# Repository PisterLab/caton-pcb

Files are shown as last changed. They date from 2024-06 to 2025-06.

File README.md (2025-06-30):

# Caton PCB: A Wireless EEG System for Concurrent TMS-EEG-fMRI

Caton is an open-source, wireless EEG system designed to address the challenges of concurrent TMS-EEG-fMRI studies. By eliminating long wires and large loop areas typical in traditional EEG systems, Caton aims to provide a safer and more effective platform for multimodal brain imaging and stimulation. This repository contains the hardware design files for the Caton project.

This work was published at ISMRM 2025.

## Overview

Concurrent TMS-EEG-fMRI measurements offer improved insights into human brain function, combining high temporal and spatial resolution with causal intervention. However, the long wires in traditional EEG systems pose substantial safety and signal integrity concerns in the MRI environment.

This project introduces a wireless EEG system based on the Single Chip Micro Mote (SCµM). The goal is to enable safer, more effective multimodal brain imaging studies by minimizing wire-induced artifacts and risks. We have developed and validated a prototype system that integrates the SCµM-3C with the Texas Instruments ADS1299 on an MRI-safe PCB. Our results show stable wireless operation from within the MRI bore with minimal disruption from MRI sequences.

## System Architecture

The Caton system is designed to be modular, allowing for flexible development and testing. The main components are the `Caton-M-TRAD` motherboard and compatible daughterboards like the `Caton-D-Q100`.

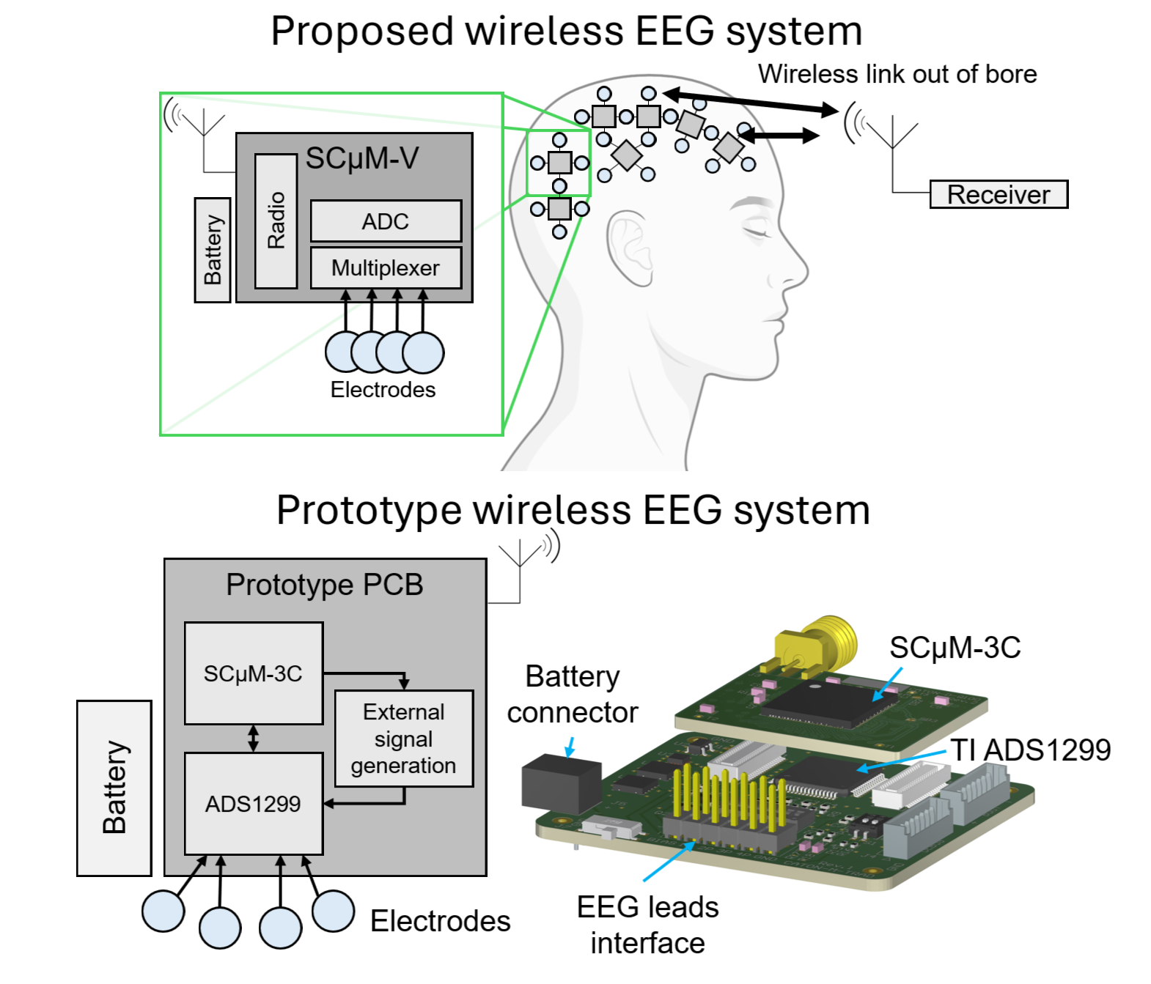
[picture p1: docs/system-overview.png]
System Overview


### Caton-M-TRAD (Motherboard)

`Caton-M-TRAD` is the main motherboard that houses the core circuitry for EEG signal acquisition and power management. It is a traditional PCB that includes:
- The Texas Instruments ADS1299 EEG analog front-end.
- Four power regulators for the different voltage domains:
    - 5V buck-boost for ADS1299 AVDD
    - 1.8V LDO for ADS1299 DVDD
    - 1.8V LDO for SCµM-3C VBAT/VDDIO
    - 1.1V LDO for SCµM-3C VDD
- 2x 20-pin mezzanine connectors for interfacing with daughterboards.
- GPIO jumpers.
- An electrode connector.

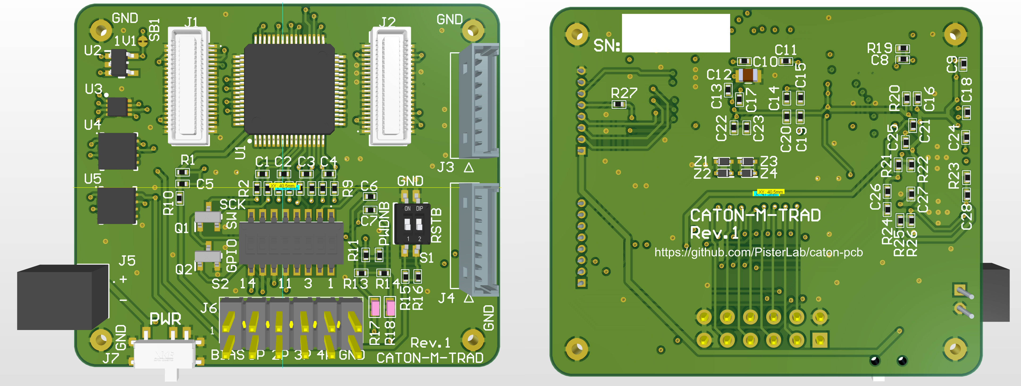
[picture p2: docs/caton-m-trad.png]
Caton-M-TRAD Diagram


### Caton-D-Q100 (Daughterboard)

`Caton-D-Q100` is a daughterboard designed to be mounted on `Caton-M-TRAD`. It contains the SCµM-3C microcontroller in a QFN100 package, which handles wireless data transmission. This modular design allows for rapid testing and iteration of the SCµM-3C unit.

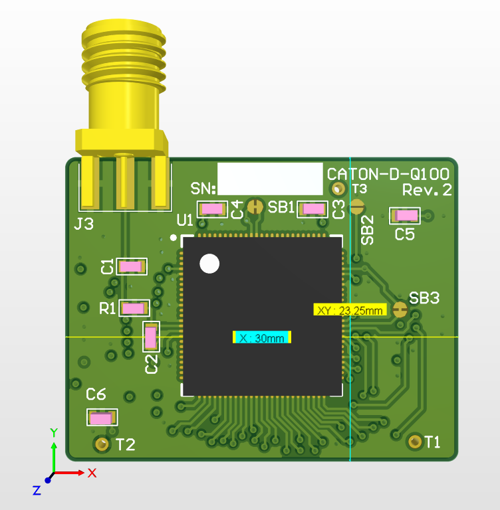
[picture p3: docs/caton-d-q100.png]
Caton-D-Q100 Diagram


### Caton Multiboard Project

The `caton-multiboard` Altium project integrates the `Caton-M-TRAD` and `Caton-D-Q100` designs into a single, cohesive system.

## Repository Contents

This repository is organized into several Altium projects and corresponding output files:

-   `caton-m-trad/`: Altium project for the main motherboard.
-   `caton-d-q100/`: Altium project for the SCµM-3C daughterboard.
-   `caton-multiboard/`: Altium multiboard project combining the mother and daughterboards.
-   `Project Outputs for caton-m-trad/`: Manufacturing files for `Caton-M-TRAD` (Gerbers, BOM, etc.).
-   `Project Outputs for caton-d-q100/`: Manufacturing files for `Caton-D-Q100`.
-   `docs/`: Documentation, including assembly guides and images.
-   `BSAC-Libs/`, `BWRC-Libs/`, `parts/`: Altium libraries for components used in the designs.

## Building the Hardware

To build the PCBs, you can use the Gerber and NC Drill files located in the `Project Outputs for ...` directories. The Bill of Materials (BOM) is also available in those directories.

Assembly guides with detailed instructions can be found in the `docs` folder:
-   [Caton-M-TRAD Assembly Guide](docs/Caton-M-TRAD-Assembly-Guide.PDF)
-   [Caton-D-Q100 Assembly Guide](docs/caton-d-q100-assembly.pdf)

## Citation

If you use this work, please cite the following publication:

Lovell, D., Maravilla, J., Lin, Y.C., Liu, C., Lustig, M., Niknejad, A.M., & Pister, K.S.J. (2025). *WIRELESS EEG SYSTEM FOR CONCURRENT TMS-EEG-fMRI*. International Society for Magnetic Resonance in Medicine (ISMRM).

And the open-source hardware:

Lovell D. Caton PCB: Prototype Wireless EEG System (Version 0.2.0) [Computer software]. GitHub 2025. doi:10.5281/zenodo.1234567.

## Acknowledgements

The authors acknowledge the support of the NIH under award number R01MH127104.

## License

This project is licensed under the BSD 3-Clause License. See the [LICENSE](LICENSE) file for details.

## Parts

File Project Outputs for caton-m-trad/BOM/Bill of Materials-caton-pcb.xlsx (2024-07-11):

Comment | Designator | Footprint | JLCPCB Part#(Optional) | Description | Quantity | Manufacturer 1 | Manufacturer Part Number 1 | Supplier 1 | Supplier Part Number 1
3.3 uF | C1, C2, C3, C4, C6, C7 | 0402 | C694161 | Capacitor, 0402, X5R, ±20% | 6 |  |  | Digi-Key | 490-13252-1-ND
10 nF | C5 | 0402 | C382730 | Capacitor, 0402, X5R, ±20% | 1 |  |  | Digi-Key | 490-13252-1-ND
0.1 uF | C8 | 0402 | C60474 | Capacitor, 0402, X7R, ±20% | 1 |  |  | Digi-Key | 490-13252-1-ND
1 uF | C9, C18, C25, C27 | 0402 | C528974 | Capacitor, 0402, X7R, ±10% | 4 |  |  | Digi-Key | 490-13252-1-ND
1.0 uF | C10, C14, C17, C20, C22, C24 | 0402 | C77009 | Capacitor, 0402, X5R, ±20% | 6 |  |  | Digi-Key | 490-13252-1-ND
100 nF | C11, C15, C19, C23 | 0402 | C60474 | Capacitor, 0402, X5R, ±20% | 4 |  |  | Digi-Key | 490-13252-1-ND
100 uF | C12 | 0805 | C141660 | Capacitor, 0805 | 1 |  |  | N.A. | N.A.
10 uF | C13 | 0402 | C315248 | Capacitor, 0402, X5R, ±20% | 1 |  |  | Digi-Key | 490-13252-1-ND
10 uF | C16, C21 | 0402 | C315248 | Capacitor, 0402, X7R, ±10% | 2 |  |  | Digi-Key | 490-13252-1-ND
4.7 uF | C26 | 0402 | C368809 | Capacitor, 0402, X5R, ±20% | 1 |  |  | Digi-Key | 490-13252-1-ND
4.7 uF | C28 | 0402 | C368809 | Capacitor, 0402, X7R, ±20% | 1 |  |  | Digi-Key | 490-13252-1-ND
54102-0404 | J1, J2 |  | N/A | 0.50mm Pitch SlimStack Receptacle, Surface Mount, Dual Row, Vertical, 2.50mm Stacking Height, Gold Plating with Nickel Barrier, 40 Circuits | 2 | Molex | 54102-0404 | Digikey | WM3781CT-ND
530470810 | J3, J4 |  | C240845 | Connector | 2
S2B-PH-KL_LF__SN_ | J5 | Plugin,P=2mm | C160237 | Connector | 1
CON_012pin_2x6 | J6 |  | C6332209 | Con 12 pins 2x6 | 1
SK-3296S-01-L1 | J7 |  | C319020 | Connector | 1
BSS138BKVL | Q1, Q2 |  | C52895 | MOSFET (N-Channel) | 2
390K | R1 | 0402 | C25782 | Resistor, 0402, ±1%, 0.05W | 1 |  |  | N.A. | N.A.
200 | R2, R3, R4, R5, R6, R7, R8, R9 | 0402 | C140185 | Resistor, 0402, ±1%, 0.05W | 8 |  |  | N.A. | N.A.
5.1K | R10 | 0402 | C25905 | Resistor, 0402, ±1%, 0.05W | 1 |  |  | N.A. | N.A.
100K | R11, R12, R13, R14, R19, R20, R22, R26 | 0402 | C25741 | Resistor, 0402, ±1%, 0.05W | 8 |  |  | N.A. | N.A.
10K | R15, R16 | 0402 | C25744 | Resistor, 0402, ±1%, 0.05W | 2 |  |  | N.A. | N.A.
0 | R17, R18 | 0603 | C21189 | Resistor, 0603 | 2 |  |  | N.A. | N.A.
46K | R21, R25 | 0402 | C100445 | Resistor, 0402, ±1%, 0.05W | 2 |  |  | N.A. | N.A.
1 | R23, R24 | 0402 | C25086 | Resistor, 0402, ±1%, 0.05W | 2 |  |  | N.A. | N.A.
10 | R27 | 0402 | C881178 | Resistor, 0402, ±1%, 0.05W | 1 |  |  | N.A. | N.A.
DHN-02F-V-T_R | S1 | SMD-4P,3.8x4.5mm | C224995 | Switch | 1
DHN-08F-T-V-T_R | S2 |  | C89711 | Switch | 1
ADS1299IPAG | U1 |  |  | Low-Noise, 8-Channel, 24-Bit Analog Front-End for Biopotential Measurement, 16 KSPS, -40 to 85 degC, 64-Pin PQFP (PAG-64), RoHS, Tube | 1 | Texas Instruments | ADS1299IPAG | Mouser | 595-ADS1299IPAG
TLV71311PDBVR | U2 |  | C205964 | Integrated Circuit | 1
LM2775DSGR | U3 |  | C473361 | Integrated Circuit | 1
LP2951ACSD/NOPB | U4, U5 |  | C2876162 | Series of Adjustable Micropower Voltage Regulators, 8-pin LLP, Pb-Free | 2 | TI National Semiconductor | LP2951ACSD/NOPB | Mouser | 926-LP2951ACSD/NOPB
MM5Z5V1T1G | Z1, Z2, Z3, Z4 | SOD-523 | C146754 | Zener Diode | 4

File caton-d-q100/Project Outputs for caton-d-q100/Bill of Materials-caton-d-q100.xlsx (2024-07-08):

Name | Designator | Footprint_Custom | Description | Quantity | Manufacturer 1 | Manufacturer Part Number 1 | Supplier 1 | Supplier Part Number 1
NP | C1, C2 | 0603 | Capacitor, 0603, X5R, ±10% | 2 |  |  | N.A. | N.A.
1 uF | C3, C5 | 0603 | Capacitor, 0603, X5R, ±10% | 2 | TDK | C1608X5R1H105K080AB | Digikey | 445-7468-1-ND
100 nF | C4, C6 | 0603 | Capacitor, 0603, X5R, ±10% | 2 | TDK | CGA3E2X7R1H104K080AA | Digikey | 445-5666-1-ND
53885-0408 | J1, J2 |  | 0.50mm Pitch SlimStack Plug, Surface Mount, Dual Row, Vertical, 2.50mm Stack Height, without Solder Tab, 40 Circuits | 2 | Molex | 53885-0408 | Digikey | WM9211CT-ND
SMA-EDGE | J3 |  | Non-Magnetic CONN SMA JACK STR 50OHM EDGE MNT | 1 | Adam Tech | RF2-143-T-17-50-G | Digikey | 2057-RF2-143-T-17-50-G-ND
0 | R1 | 0603 | Resistor, 0603 | 1 | Panasonic | ERJ-3GEY0R00V | Digikey | P0.0GCT-ND
SCuM-3C | U1 | QFN-100 |  | 1

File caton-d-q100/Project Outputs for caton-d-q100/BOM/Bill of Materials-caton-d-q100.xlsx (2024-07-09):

Name | Designator | Footprint_Custom | LCSC | Description | Quantity | Manufacturer 1 | Manufacturer Part Number 1 | Supplier 1 | Supplier Part Number 1
NP | C1, C2 |  |  | Capacitor, 0603, X5R, ±10% | 2 |  |  | N.A. | N.A.
1 uF | C3, C5 |  |  | Capacitor, 0603, X5R, ±10% | 2 | TDK | C1608X5R1H105K080AB | Digikey | 445-7468-1-ND
100 nF | C4, C6 |  |  | Capacitor, 0603, X5R, ±10% | 2 | TDK | CGA3E2X7R1H104K080AA | Digikey | 445-5666-1-ND
53885-0408 | J1, J2 |  |  | 0.50mm Pitch SlimStack Plug, Surface Mount, Dual Row, Vertical, 2.50mm Stack Height, without Solder Tab, 40 Circuits | 2 | Molex | 53885-0408 | Digikey | WM9211CT-ND
SMA-EDGE | J3 |  |  | Non-Magnetic CONN SMA JACK STR 50OHM EDGE MNT | 1
0 | R1 |  |  | Resistor, 0603 | 1 | Panasonic | ERJ-3GEY0R00V | Digikey | P0.0GCT-ND
SCuM-3C | U1 |  |  |  | 1

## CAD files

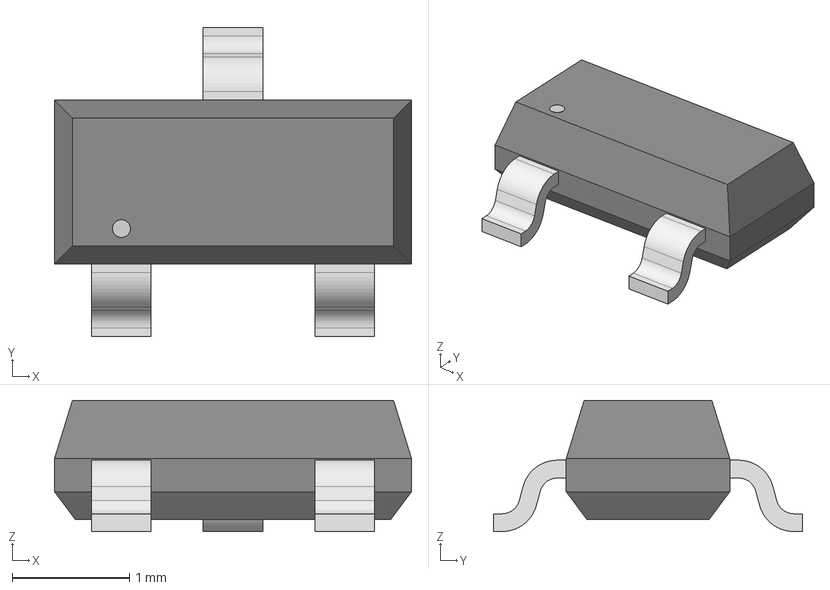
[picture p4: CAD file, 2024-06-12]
parts/bss138/SOT-23_3L_ONS.step
3.05 x 2.64 x 1.12 mm

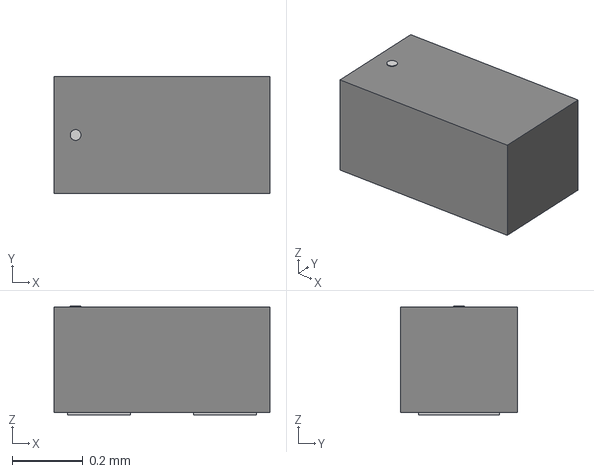
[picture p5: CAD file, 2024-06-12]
parts/gdz5v1lp3-7/CR_V1LP3-7_DIO.step
0.61 x 0.33 x 0.307 mm

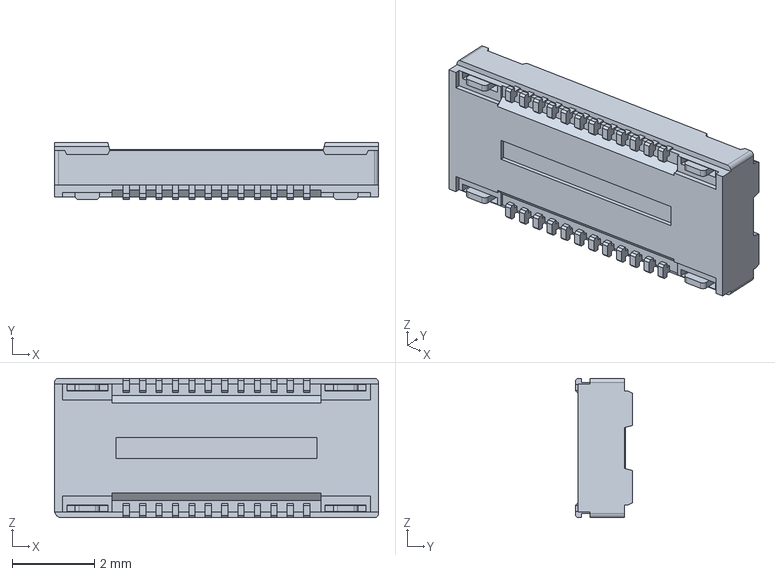
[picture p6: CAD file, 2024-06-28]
BSAC-Libs/513382474/513382474.stp
7.90 x 1.40 x 3.40 mm

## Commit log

2024-06-11 WIP caton-pcb draft
    [400250.PcbDoc, 400250.PcbLib, BWRC.SchLib, caton-ads1299.SchDoc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]
2024-06-12 Caton sch progress, zener & mosfet parts
    [BSS138.PcbLib, BSS138.SchLib, CR_V1LP3-7_DIO.step, GDZ5V1LP3-7.PcbLib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]
2024-06-13 Schematic improvments, introduction of lm2775
    [Components - 12.06.24 - 00.46.PcbLib, Components - 12.06.24 - 00.46.SchLib, caton-ads1299.SchDoc, caton-nrf52840.SchDoc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]
2024-06-28 scum-3c schlib, pcblib, caton-scum3c.SchDoc
    [BSAC.PcbLib, BSAC.SchLib, caton-ads1299.SchDoc, caton-pcb.PrjPcb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]
2024-06-28 WIP multiboard
    [513382474.PcbLib, 513382474.SchLib, 513382474.stp, BSAC.PcbLib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]
2024-06-28 Multiboard project
    [caton-motherboard.PrjPcb, caton-scum3c.SchDoc, caton-top.SchDoc]
2024-07-02 LM2775 regulator, schematic progress
    [BSAC.PcbLib, BSAC.SchLib, LM2775DSGR.PcbLib, LM2775DSGR.SchLib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]
2024-07-02 Added Caton-D-Q100
    [caton-d-q100.PcbDoc, caton-d-q100.PrjPcb, caton-scum3c.SchDoc]
2024-07-02 Reorganization of the project
    [caton-d-q100.PcbDoc, caton-m-trad.PrjPcb, caton-top.SchDoc]
2024-07-02 caton-d-q100 progress
    [400250.PcbDoc, BSAC.PcbLib, BSAC.SchLib, caton-ads1299.SchDoc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]
2024-07-02 Copy components from SamacSys to BSAC libss
    [BSAC.PcbLib, BSAC.SchLib]
2024-07-03 Major progress on all PCBs
    [BSAC.PcbLib, BSAC.SchLib, GDZ5V1LP3-7.PcbLib, caton-ads1299.SchDoc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]
2024-07-03 DRC rules for JLC PCB
    [BSAC.SchLib, caton-d-q100.PcbDoc, caton-d-q100.PrjPcb, caton-d-q100.SchDoc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]
2024-07-03 More progress on all fronts
    [BSAC.PcbLib, BSAC.SchLib, caton-d-q100.PcbDoc, caton-d-q100.PrjPcb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]
2024-07-03 Debug connector, battery connector
    [BSAC.PcbLib, BSAC.SchLib, caton-top.SchDoc, caton.PcbDoc]
2024-07-05 Nearly finished Caton-D-Q100
    [Bill of Materials-caton-d-q100.xlsx, caton-d-q100.GBL, caton-d-q100.GBO, caton-d-q100.GBP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]
2024-07-05 Updates to caton-d-q100
    [caton-d-q100.PcbDoc, caton-d-q100.SchDoc]
2024-07-06 caton-d-q100 edge launch SMA, silkscreen, decap
    [BSAC.SchLib, caton-d-q100.PcbDoc, caton-d-q100.PrjPcb, caton-d-q100.SchDoc]
2024-07-06 Caton-d-q100 complete
    [BSAC.PcbLib, BSAC.SchLib, Bill of Materials-caton-d-q100.xlsx, caton-d-q100.GBL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]
2024-07-07 caton-d-q100 sch updates
    [caton-d-q100.SchDoc]
2024-07-07 caton-d-q100 Rev.1 release
    [Bill of Materials-caton-d-q100.xlsx, caton-d-q100.GBL, caton-d-q100.GBO, caton-d-q100.GBP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]
2024-07-08 caton-d-q100 submitted x2
    [BSAC.PcbLib, BSAC.SchLib, Bill of Materials-caton-d-q100.xlsx, caton-d-q100.GBL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]
2024-07-08 floorplan caton-m-trad
    [BSAC.PcbLib, BSAC.SchLib, caton-ads1299.SchDoc, caton-d-q100.PcbDoc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]
2024-07-08 Floorplanning, routing, CATON-M-TRAD
    [caton-top.SchDoc, caton.PcbDoc]
2024-07-09 Random progress
    [caton-top.SchDoc, caton.PcbDoc]
2024-07-09 Job files and gerbers
    [Bill of Materials-caton-d-q100.xlsx, caton-d-q100.GBL, caton-d-q100.GBO, caton-d-q100.GBP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]
2024-07-09 Pushing changes to transfer
    [caton-m-trad.PrjPcb, caton.PcbDoc]
2024-07-09 Misc changes
    [caton.PcbDoc]
2024-07-10 Caton-M-Trad initial submission
    [BSAC.PcbLib, BSAC.SchLib, caton-ads1299.SchDoc, caton-m-trad.PrjPcb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]
2024-07-10 Complete bom for caton-m-trad
    [Bill of Materials-caton-pcb.xlsx, caton-m-trad.PrjPcb, caton-top.SchDoc, caton.GBL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]
2024-07-11 Caton-M-TRAD submitted
    [Bill of Materials-caton-pcb.xlsx, caton-d-q100.PcbDoc, caton-m-trad.PrjPcb, caton-top.SchDoc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]
2024-07-11 Sch updates
    [caton-d-q100.SchDoc]
2024-07-15 Caton-M-TRAD assembly guide
    [BSAC.PcbLib]
2024-09-05 Caton-M-TRAD Rev.2 - fixed LP2951 SD pin, tied CLKSEL high
    Disconnect shutdown of LP2951 **this is confirmed to be the cause of 2.2V instead of 1.8V**
    Fix the ADS1299 CLKSEL, which was left floating and should have been tied to DVDD
    [caton-top.SchDoc]
